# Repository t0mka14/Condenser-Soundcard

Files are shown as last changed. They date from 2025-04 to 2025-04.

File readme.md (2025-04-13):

# Condenser soundcard

High gain USB soundcard with 5V power for headset condenser microphones. This repo contains Kicad design files for a USB soundcard using [PCM2912](https://www.ti.com/lit/ds/symlink/pcm2912a.pdf?ts=1744521427834&ref_url=https%253A%252F%252Fwww.ti.com%252Fproduct%252FPCM2912A). PCM2912 is one of a few publicly available USB audio codecs. It contains USB 2.0 FS, mic input with integrated optional 20db pre amp (sadly only hw controlled), L a R outputs. We use this soundcard in our team at FEE CTU to record patients with various neurodegenerative diseases (<https://sami.fel.cvut.cz/>).

## Table of Contents

- [Hardware](#hardware)
- [Case](#case)

## Hardware
Headworn condenser microphones need DC bias voltage to work properly. They contain JFET integrated into the microphone capsule, amplifying the signal from the electret element. The voltages have different ranges, depending on manufacturer, but they often include 5V. Since PCM2912 ouputs only 2.7V with 5V USB power, some modifications to the catalogue design were needed. 

The first though was to take the USB power, filter it a bit and voala, you have 5V. That didn't work at all. Altought on the scope, the voltage seemed completely fine and reasonably clear, there was huge noise in the input audio. It turns out, the TI engineers use some technique to get rid of the digital USB noise and as a result AGND is not connected to GND. So don't mess with the grounds on the PCB! 

Since the mic takes only around 200 uA of current, i decided to use charge pump and take that 2.7V from original mic bias and double it. This works fine and doesn't add any noise to the audio path. One thing they don't mention in the datasheet - the bias turns off when microphone is not in use,

Since we manufactured more than 300 of these, i made a 5x6 panel for the assembly using KiKit with custom mousebite positions. The project for that is in the folder "panel".

## Case
In the folder "case" the are stl files for 3D print as well as 3mf files for color print on Prusa multimaterial. The case is from two parts that "click" together. It holds kinda good just like that, but you can secure it using M2 screw (we do that).
<p align="center">
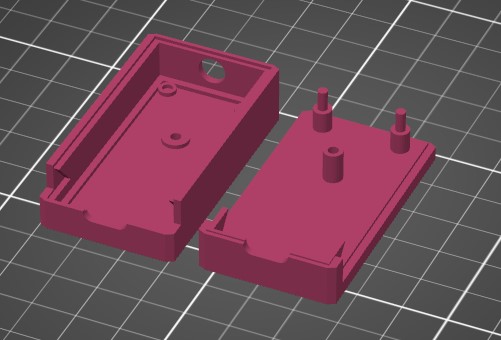
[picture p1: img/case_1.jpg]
Z570M pcb
    
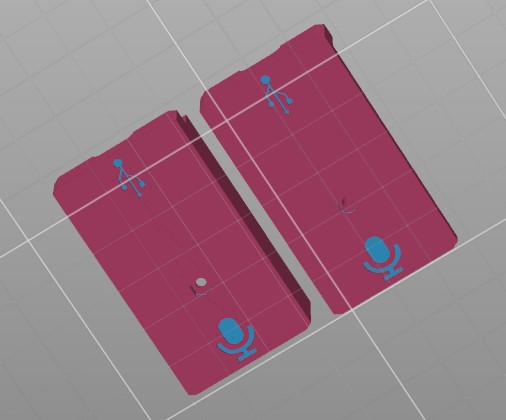
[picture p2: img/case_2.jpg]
Z570M on socket
    
</p>

## Measurements
Since we were originally wanted just to buy a finished solution, I measured frequency response of various USB soundcards available in the market.
Here is a frequency response measured using R&S UPV and Audacity. I used the UPV generator to input sine wave into the mic input and then measured DB using Audacity from 4s samples.
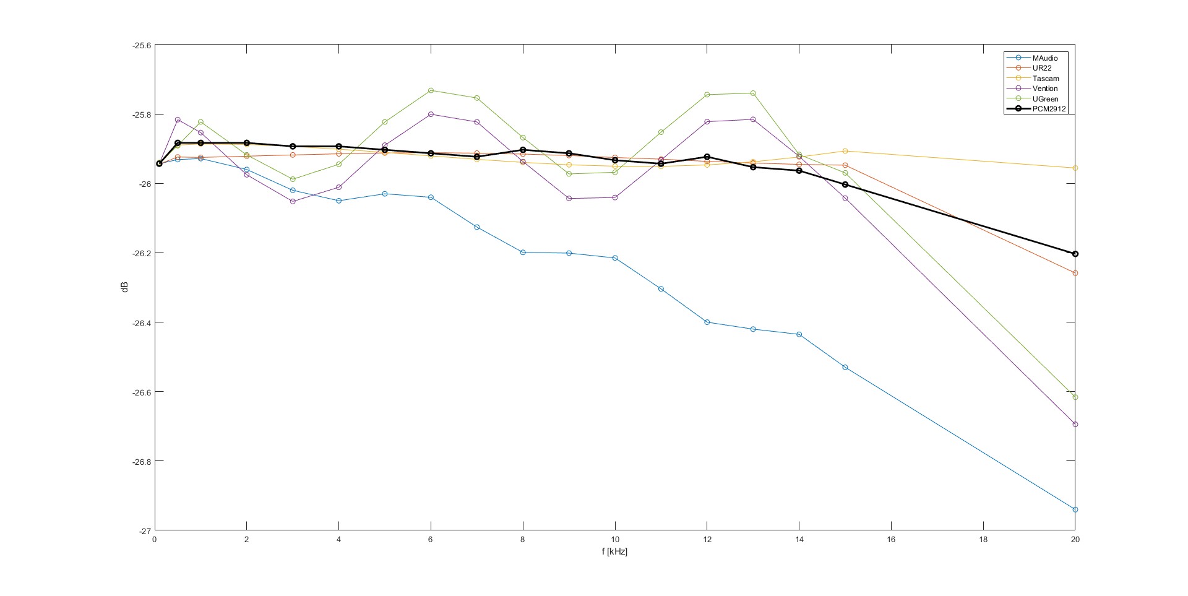
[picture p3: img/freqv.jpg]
Frequency response

Since price for one of these PCM soundards is around 15$ i think it does quite good compared to 180$ Tascam DR-40X.
I also measured the amplitude spectrum using ARTA, there is PCM
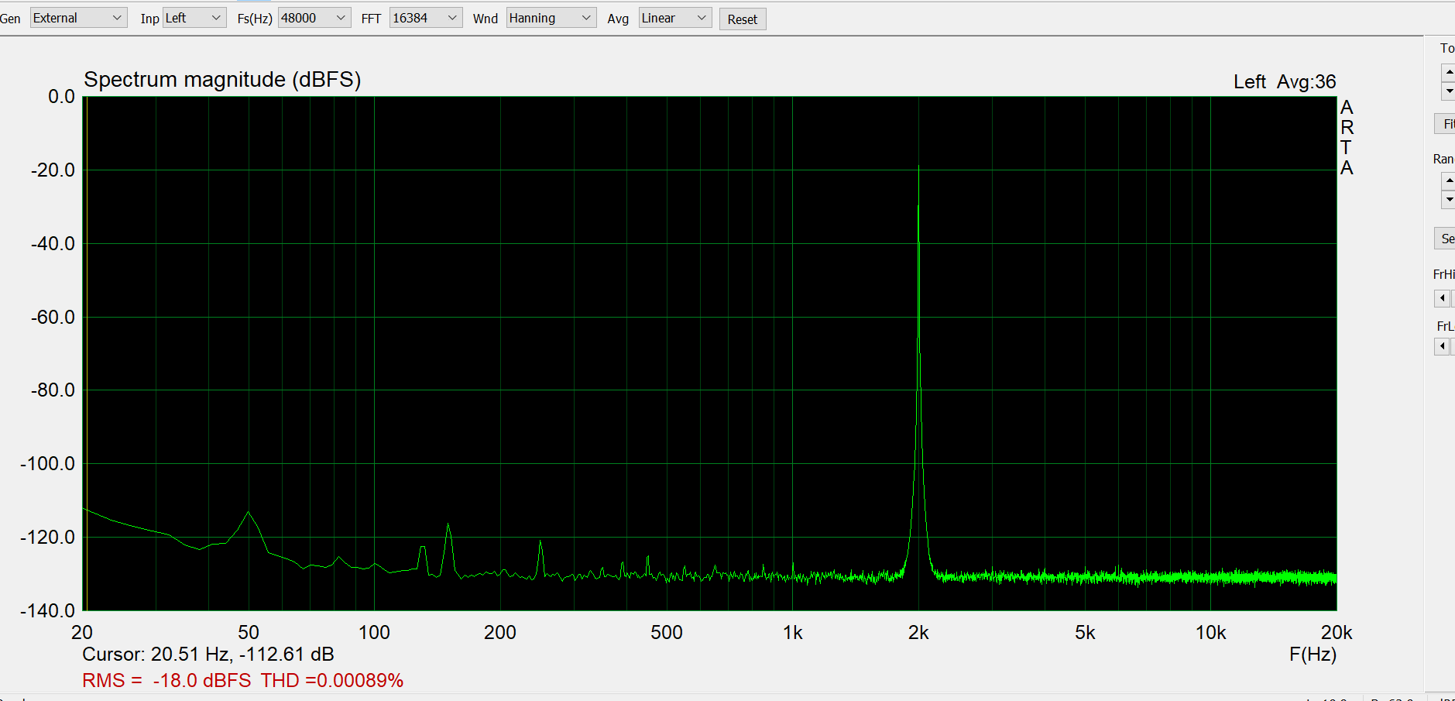
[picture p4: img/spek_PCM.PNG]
PCM2912

 and the DR-40X for comparison.
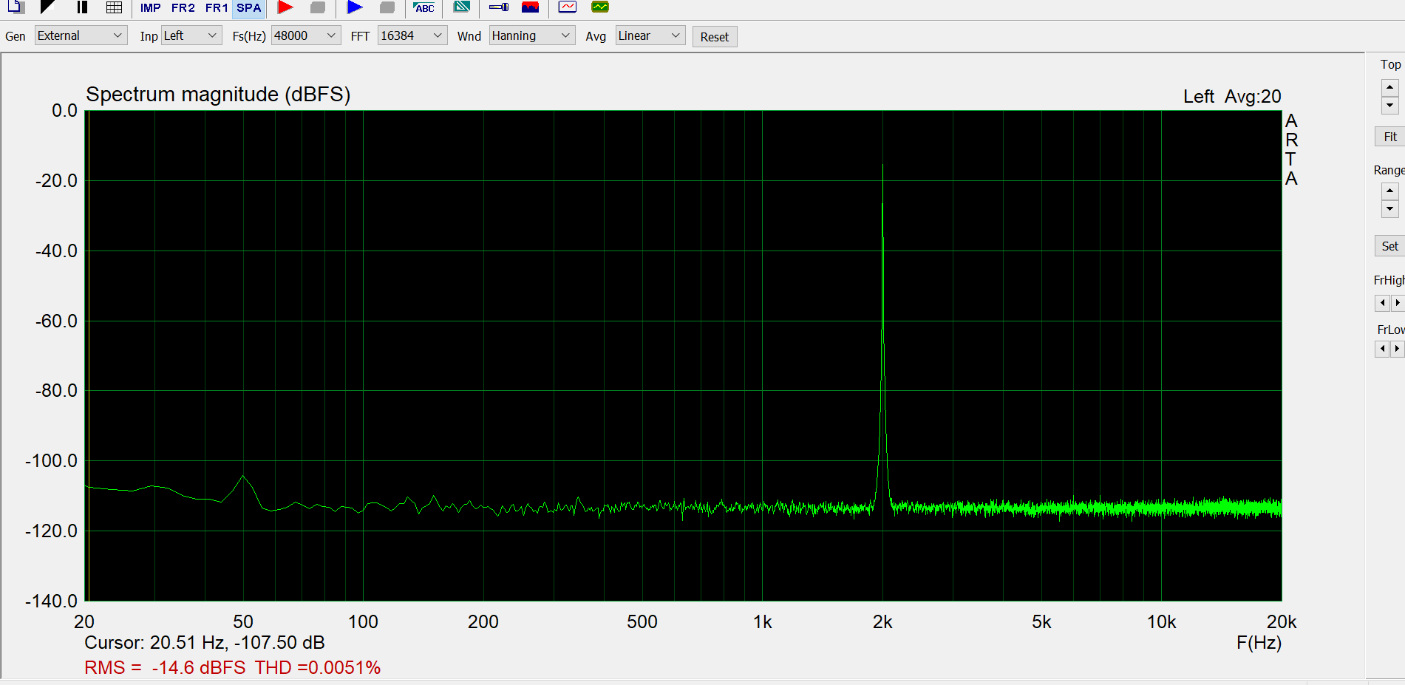
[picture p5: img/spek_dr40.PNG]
DR-40X


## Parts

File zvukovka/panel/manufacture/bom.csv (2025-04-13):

Reference | Value | Footprint | MPN | note | Qty
C1, C8, C11, C14, C17, C18 | 1u | Capacitor_SMD:C_0805_2012Metric |  | X5R nebo X7R, >16V,10% | 6
C2, C3 | 22p | Capacitor_SMD:C_0805_2012Metric |  | X5R nebo X7R, >16V,10% | 2
C6, C10, C13, C15 | 3.3u | Capacitor_SMD:C_0805_2012Metric |  | X5R nebo X7R, >16V,10% | 4
C7 | 100n | Capacitor_SMD:C_0805_2012Metric |  | X5R nebo X7R, >16V,10% | 1
C9 | 0.47u | Capacitor_SMD:C_0805_2012Metric |  | X5R nebo X7R, >16V,10% | 1
D1 | D_Schottky | Diode_SMD:D_SMA | SS26A+ |  | 1
J1 | USB_C_Receptacle_USB2.0 | zvukovka_2:Conn_USB_C_Socket_Molex_2171790001 | 217179-0001 |  | 1
J2 | Conn_01x02_Pin | Connector_PinHeader_2.54mm:PinHeader_1x02_P2.54mm_Vertical |  | NEOSAZOVAT | 1
L1 | 1u | zvukovka:SRP2012TMA | SRP2012TMA-1R0M |  | 1
M1-M3 | MountingHole | MountingHole:MountingHole_2.2mm_M2_DIN965 |  |  | 3
R1, R2 | 33 | Resistor_SMD:R_0805_2012Metric |  | 1% | 2
R3 | 1.5k | Resistor_SMD:R_0805_2012Metric |  | 1% | 1
R4 | 1M | Resistor_SMD:R_0805_2012Metric |  | 1% | 1
R5, R7 | 5k1 | Resistor_SMD:R_0805_2012Metric |  | 1% | 2
R6 | 5k | Resistor_SMD:R_0805_2012Metric |  | 1% | 1
U1 | AudioJackShare | zvukovka_2:K3612A | K3612A | https://www.gme.cz/v/1501048/k3612a-jack-35-stereo | 1
U2 | PCM2912APJTR | zvukovka_2:TQFP-32_7x7mm_P0.8mm_netTie | PCM2912APJT |  | 1
U3 | LM2766 | Package_TO_SOT_SMD:SOT-23-6 | LM2766M6X/NOPB |  | 1
Y2 | Crystal_GND24 | Crystal:Crystal_SMD_7050-4Pin_7.0x5.0mm | EA5070PA20-6.000M TR |  | 1

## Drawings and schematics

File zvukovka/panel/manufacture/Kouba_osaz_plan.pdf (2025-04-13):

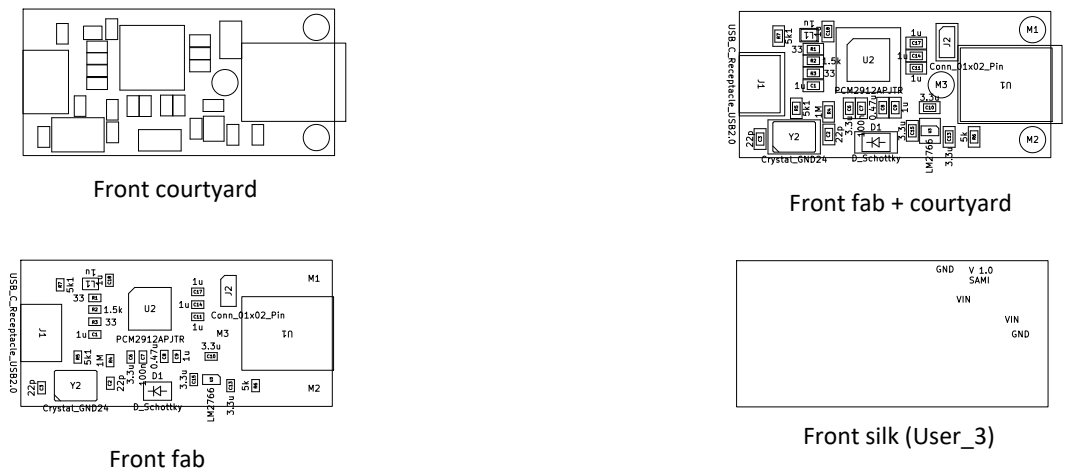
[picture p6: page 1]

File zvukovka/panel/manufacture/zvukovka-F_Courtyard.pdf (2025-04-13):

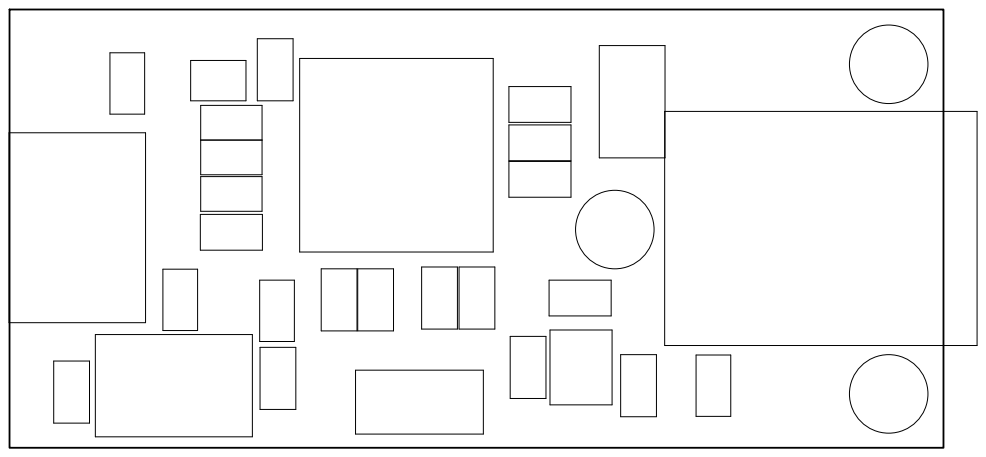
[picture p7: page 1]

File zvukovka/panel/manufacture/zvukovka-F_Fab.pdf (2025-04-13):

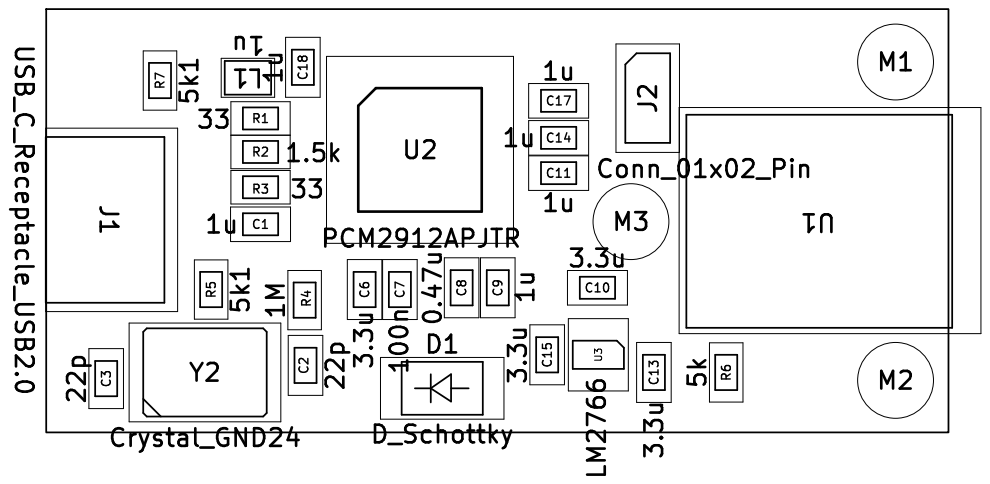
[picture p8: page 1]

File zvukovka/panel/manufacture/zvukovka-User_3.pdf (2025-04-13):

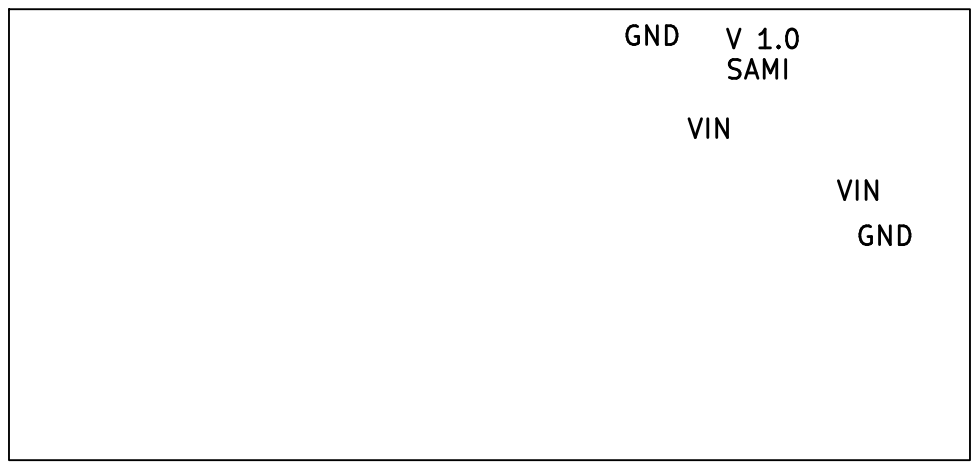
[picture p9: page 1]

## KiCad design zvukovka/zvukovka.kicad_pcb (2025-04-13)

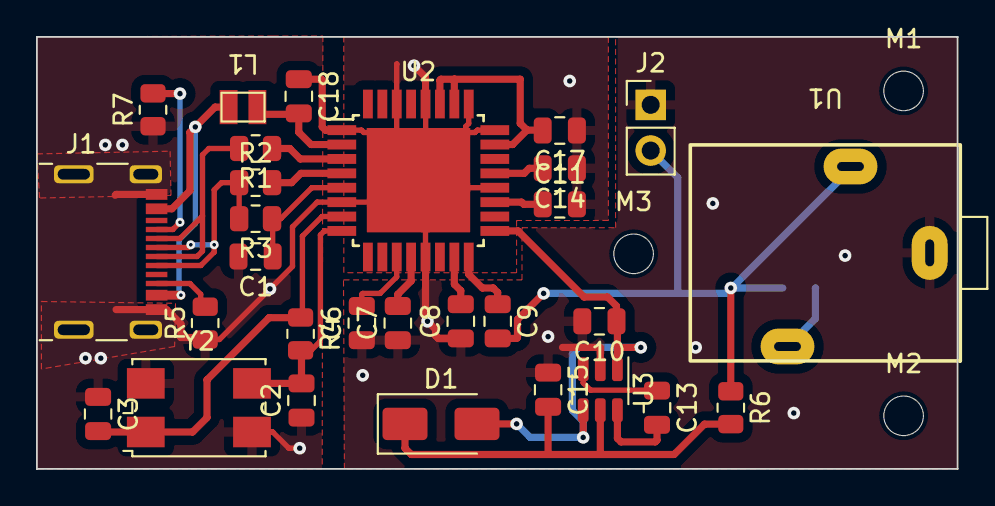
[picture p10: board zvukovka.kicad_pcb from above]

Board: 2 copper layers, 51.2 x 24.0 mm, 33 parts (1 on the bottom side), 28 nets.

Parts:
C1, C8, C11, C14, C17, C18: 1u; C_0805_2012Metric
C2, C3: 22p; C_0805_2012Metric
C6, C10, C13, C15: 3.3u; C_0805_2012Metric
C7: 100n; C_0805_2012Metric
C9: 0.47u; C_0805_2012Metric
D1: D_Schottky; D_SMA
J1: USB_C_Receptacle_USB2.0; Conn_USB_C_Socket_Molex_2171790001
J2: Conn_01x02_Pin; PinHeader_1x02_P2.54mm_Vertical
L1: 1u; SRP2012TMA
M1, M2, M3: MountingHole_2.2mm_M2_DIN965
R1, R2: 33; R_0805_2012Metric
R3: 1.5k; R_0805_2012Metric
R4: 1M; R_0805_2012Metric
R5, R7: 5k1; R_0805_2012Metric
R6: 5k; R_0805_2012Metric
R8: R; R_0805_2012Metric
U1: AudioJackShare; K3612A
U2: PCM2912APJTR; TQFP-32_7x7mm_P0.8mm_netTie
U3: LM2766; SOT-23-6
Y2: Crystal_GND24; Crystal_SMD_7050-4Pin_7.0x5.0mm

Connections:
/USBC_D+: J1.A6 (D+), J1.B6 (D+), R2.1, R3.2
/XTO: C3.2, R4.1, U2.7 (XTO), Y2.1
CAPOUT: C15.2, D1.1 (K), R6.2, U3.5 (VOUT)
GND: C11.2, C14.1, C17.1, U2.20 (HGND), U2.24 (POWER), U2.25 (PGND), U2.28 (TEST0), U2.30 (MMUTE)
GND1: C18.1, U2.1 (BGND)
GNDA: C6.1, C7.1, C8.1, C10.2, C15.1, J2.1, U1.1, U2.13 (AGND), U3.2 (GND)
GNDD: C1.2, C2.1, C3.1, J1.A1 (GND), J1.S1 (SHIELD), R5.1, R7.1, U2.6 (DGND), Y2.2, Y2.4
unnamed: C10.1, D1.2 (A), U2.17 (MBIAS), U3.1 (V+), U3.4 (SD)
unnamed: J1.A5 (CC1), R7.2
unnamed: J1.B5 (CC2), R5.2
unnamed: J1.A7 (D-), J1.B7 (D-), R1.2
unnamed: J1.A4 (VBUS), L1.2
unnamed: R8.1, U1.3
unnamed: R2.2, U2.4 (D+)
unnamed: R1.1, U2.3 (D-)
unnamed: C17.2, U2.23 (MAMP), U2.26 (VCCP), U2.27 (TEST1)
unnamed: C18.2, L1.1, U2.2 (VBUS)
unnamed: C8.2, U2.15 (VCCA)
unnamed: C11.1, U2.19 (VCCL)
unnamed: C14.2, U2.21 (VCCR)
unnamed: C6.2, U2.11 (VCOM1)
unnamed: C7.2, U2.12 (VCOM2)
unnamed: C1.1, R3.1, U2.5 (VDD)
unnamed: C9.1, U2.16 (VIN)
unnamed: C2.2, R4.2, U2.8 (XTI), Y2.3
unnamed: C13.2, U3.6 (CAP+)
unnamed: C13.1, U3.3 (CAP-)
VIN: C9.2, J2.2, R6.1, R8.2, U1.2

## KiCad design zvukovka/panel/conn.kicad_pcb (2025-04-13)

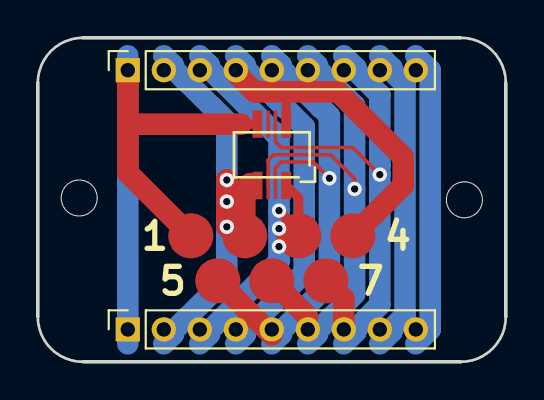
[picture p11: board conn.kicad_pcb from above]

Board: 2 copper layers, 26.0 x 18.0 mm, 6 parts (0 on the bottom side), 9 nets.

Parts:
H1, H2: MountingHole; MountingHole_2mm
J1: IN; PinSocket_1x09_P2.00mm_Vertical
J2: OUT; PinSocket_1x09_P2.00mm_Vertical
J3: POGO; pogo_pads_4_3
J4: Molex; molex-505004-0812

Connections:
1: J1.1, J2.1, J3.1, J4.8
2: J1.2, J2.2, J3.2, J4.7
3: J1.3, J2.3, J3.3, J4.1
4: J1.4, J2.4, J3.4, J4.2
5: J1.5, J2.5, J3.5, J4.3
6: J1.6, J2.6, J3.6, J4.5
7: J1.7, J2.7, J3.7, J4.4
8: J1.8, J2.8
9: J1.9, J2.9
